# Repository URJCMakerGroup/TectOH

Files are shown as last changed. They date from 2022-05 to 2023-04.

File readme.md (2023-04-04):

# Tectonic Open Hardware (TectOH) Sandbox

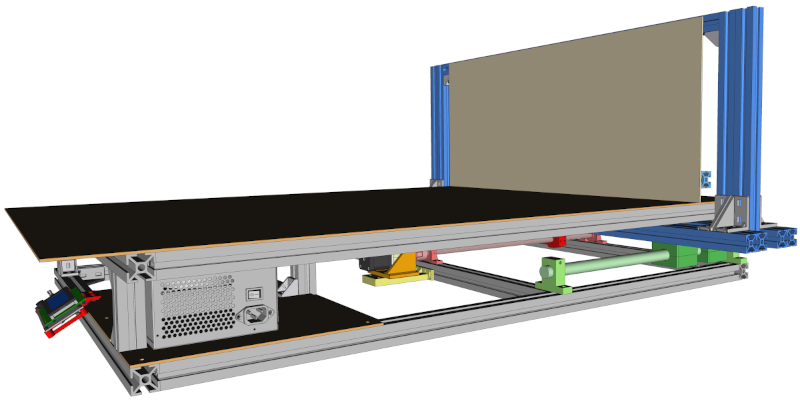
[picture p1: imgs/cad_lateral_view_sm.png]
Sandbox CAD image


Low-cost Open-Hardware scientific and educational device for tectonic analogue modelling. See Wikipedia entry on [tectonic analogue modeling](https://en.wikipedia.org/wiki/Analogue_modelling_%28geology%29).

It can move at speeds from 1 mm/h to 100 mm/h.

The stroke of the gantry is 270 mm but it can be easily customized for other lengths.

The cost of the components is no more than 500 €, although for increased performance, precision components can be used at higher cost.

There are some [optional components](#distance-monitoring) for **measuring the distance** that would increase the cost.

It is not too complicated to build. It should be simpler than building a 3D printer or CNC.

For a more theoretical information about the system and detailed explanations of the experiments, you can check the paper:
[Designing Low-Cost Open-Hardware Electromechanical Scientific Equipment: A Geological Analogue Modeling Sandbox](https://doi.org/10.1109/ACCESS.2023.3262617)

This is the second version of the Open Hardware Sandbox. [Link to the first version](https://github.com/URJCMakerGroup/TFG-Cristina-Fernandez)

----

## License

Hardware License: [CERN-OHL-S 2.0](cern_ohl_s_v2.txt)

Software License: [LGPL 3.0 or later](License.md)

Documentation License: [CC BY 4.0](https://creativecommons.org/licenses/by/4.0/)

license summary

ES000033

This device is [certified open hardware](https://certification.oshwa.org/es000033.html) by the [Open Source Hardware Association](https://www.oshwa.org/).

----

## Bill of materials

It is about 500€ without taxes and shipping costs.

There could be cheaper alternatives in your area.

You can use more expensive mechanical components to increase the overall precision of the system

[Sandbox bill of materials (.ods file)](tectoh_bom.ods)

----

## Assembly

[Sandbox assembly](./assembly/.)

----

## Firmware

[Arduino code of the Sandbox](./firmware/.)

----

## Distance monitoring

[Optical or magnetic linear sensor](./optional/.) can be included in the Sandbox to monitor the displacement.
These are optional subsystems, but they are very helpful to calibrate the Sandbox.

This section includes graphs of the **results** and Python scripts to analyze the data from the magnetic sensor.

----

## User guide

[Sandbox user guide](./userguide/.)

----

## Pictures

### Sandbox experiment

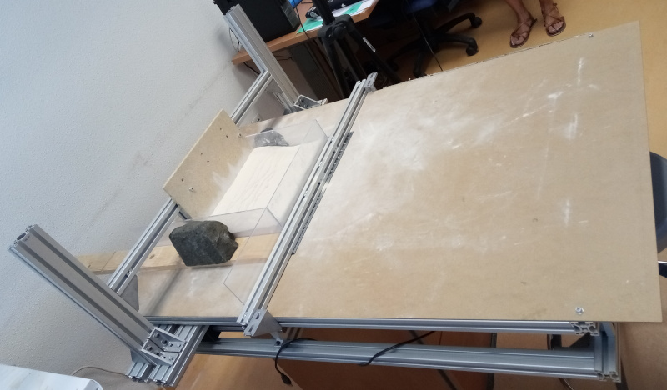
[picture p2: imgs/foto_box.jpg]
Experiment


### The Sandbox pushing a 10-kg sandpile

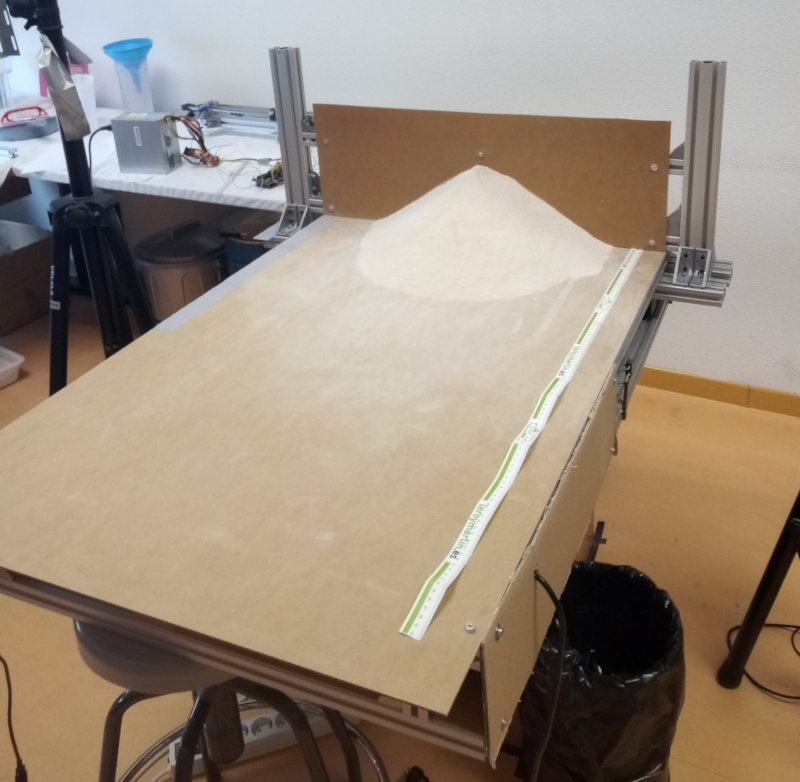
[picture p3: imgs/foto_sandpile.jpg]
Picture 10-kg sandpile


The whole experiment took 3 hours and 45 minutes, the following sequence is fast-forwarded.

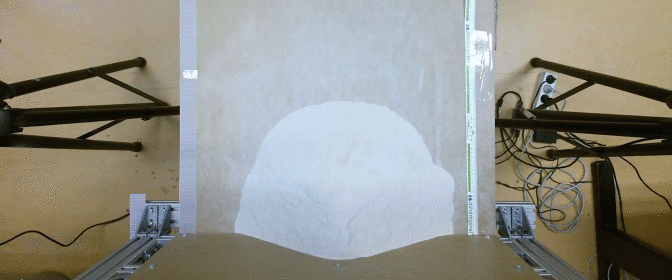
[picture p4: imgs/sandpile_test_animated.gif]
Sandpile test


### The Sandbox pushing a 5-kg sand load constrained within a box

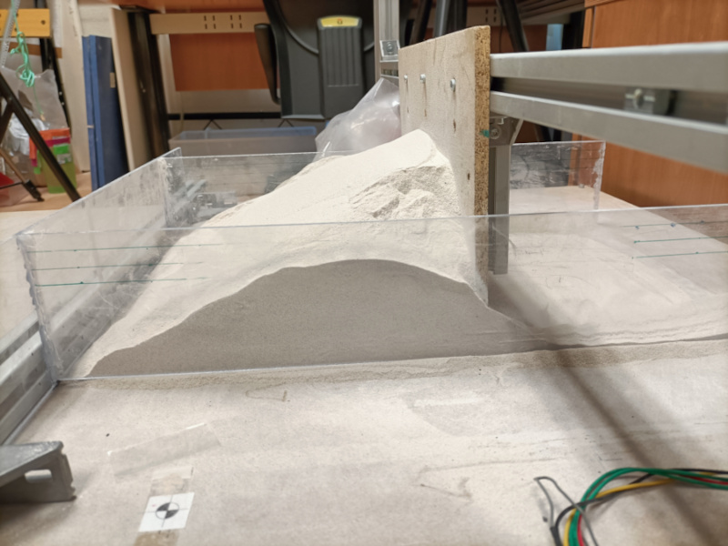
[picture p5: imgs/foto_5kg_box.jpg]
Picture 5-kg box


### The Sandbox in a geological experiment

The experiment took 4 hours (at the end the camera was moved)

Sandpile test

----

## Contributors

This work has been developed at [Universidad Rey Juan Carlos](https://www.urjc.es/) in Spain. It has been a collaboration between the Area of Electronic Technology and the group [Tecvolrisk](https://tecvolrisk.wixsite.com/website) of the Area of Geology.

### Area of Electronic Technology:

- [Felipe Machado](https://github.com/felipe-m/)
- [Rubén Nieto](https://gestion2.urjc.es/pdi/ver/ruben.nieto)
- [Susana Borromeo](https://gestion2.urjc.es/pdi/ver/susana.borromeo)

### Tecvolrisk (Area of Geology)

- [Marta Rincón](https://gestion2.urjc.es/pdi/ver/marta.rincon)
- [Sandra González-Muñoz](https://tecvolrisk.wixsite.com/website/sandra-gonz%C3%A1lez-mu%C3%B1oz)
- [Fidel Martín-González](https://gestion2.urjc.es/pdi/ver/fidel.martin)

### Students

Some students have collaborated in the project doing their capstone project in Industrial Engineering.

- [Adrián Zeus Román](https://github.com/zeus97roman/tfg): Initial project
- [Cristina Fernández García](https://github.com/cfg97/TFG-Cristina-Fernandez): Finished first version
- [David Muñoz Bernal](https://github.com/davidmubernal/MakerWorkbench): FreeCAD workbench that includes many CAD parts of the project 
- [Javier Letón](https://github.com/jleton10/TFG_Javier_Leton): Added the linear optical sensor
- [Alicia Merchán](https://github.com/AliciaMH/TFGAliciaMerchan): future work in adding a second degree of freedom

----

## Citation

If you use this hardware, you may want to cite the research article:
[Designing Low-Cost Open-Hardware Electromechanical Scientific Equipment: A Geological Analogue Modeling Sandbox](https://doi.org/10.1109/ACCESS.2023.3262617)

F. Machado et al., "Designing Low-Cost Open-Hardware Electromechanical Scientific Equipment: A Geological Analogue Modeling Sandbox," in IEEE Access, vol. 11, pp. 31716-31746, 2023, doi: 10.1109/ACCESS.2023.3262617.

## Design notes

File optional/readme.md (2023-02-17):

# Optional components

He have used two linear sensor to measure the displacement:

- Optical linear sensor
- [High-resolution magnetic sensor](#high-resolution-magnetic-sensor)

----

## Optical linear sensor

One is a optical linear sensor that has been savaged from an old printer. The sensor is 150 LPI (lines per inch) so it has a resolution around 169 μm per line.

The Arduino code includes the reading and display of the current position. However, since this component is optional, the Sandbox will work even if it is not installed.

The optical sensor that has been used is similar to the [AEDS-962x](./linear_optical_sensor/aeds-962x_150lpi.pdf)

The sensor needs a small circuit to work and to install it requires some soldering skills, especially if you to take it out from a printer.

A 330 Ohm resistor has to be included between 5V and the led emitter of the sensor. As shown in the following figure:

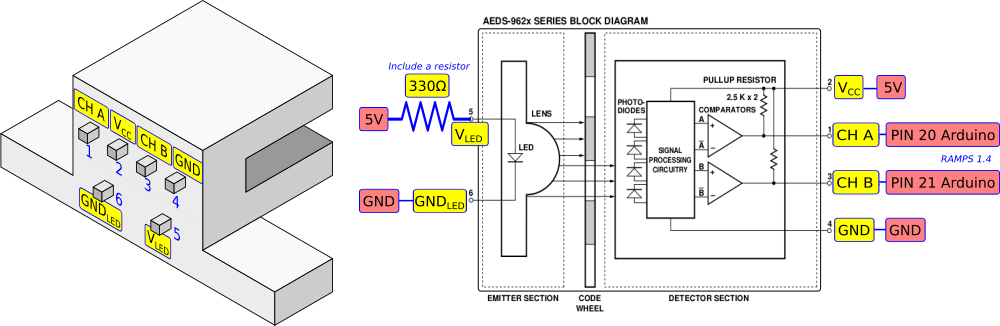
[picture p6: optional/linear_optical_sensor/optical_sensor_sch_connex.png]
Sensor connection


We have used a simple board to solder the sensor pins and the 330Ω resistor.

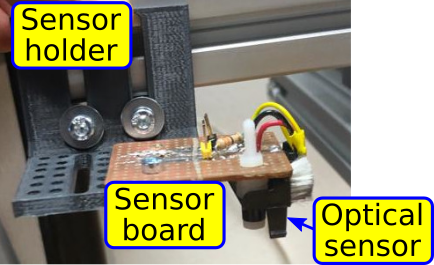
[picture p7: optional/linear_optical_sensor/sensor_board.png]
Sensor board


The following pictures show how the optical codestrip and the sensor is arranged

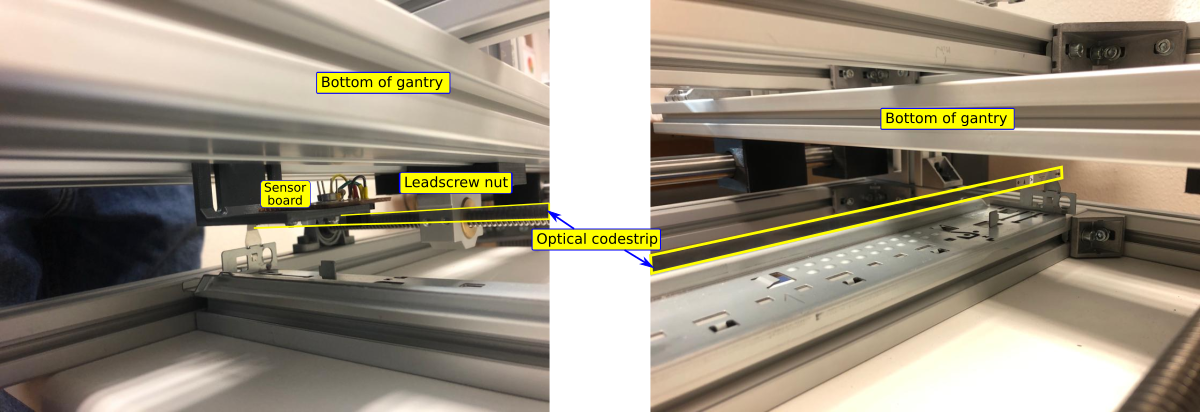
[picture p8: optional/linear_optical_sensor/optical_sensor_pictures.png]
Optical sensor arrangement


More information about these sensors:

- https://reprap.org/wiki/Optical_encoders_01
- https://cuverita.wordpress.com/2013/06/30/how-to-master-an-hp-printer-optical-encoder-carriage/

If you are going to buy one, maybe you could get the HEDS-973x Series. **Disclaimer:** We have not tried them, but they seem similar, and even simpler because the led do not have an independent power supply.

[HEDS-973x](./linear_optical_sensor/heds_973x.pdf)

----

## High resolution magnetic sensor

Since it is a high resolution sensor (less than 500 nm), the sensor will constantly update the measurement, as a consequence, it would demand too much attention from the Arduino and the system would not work properly. 
To solve this problem, we have used an external FPGA to measure the position. This sensor has been used only to validate the positional accuracy of the system.

We have used the breakout board, so it is not necessary to solder the chip, and it came with a magentic strip. The strip is small, but enough to make the experiments.

This is the [datasheet](./as5311_magn_sens/as5311_board.pdf) of the AS5311-TS-EK-AB adapter board.

And some links to suppliers where you can buy it:

- [Digikey](https://www.digikey.es/en/products/detail/ams-osram/AS5311-TS-EK-AB/3828353)
- [RS](https://es.rs-online.com/web/p/kits-de-desarrollo-de-sensores/2329691)
- [Mouser](https://eu.mouser.com/ProductDetail/ams-OSRAM/AS5311-TS_EK_AB?qs=Rt6VE0PE%2FOfQFCqoE7AuPw%3D%3D)
- [Farnell](https://es.farnell.com/ams-osram-group/as5311-ts-ek-ab/kit-placa-adapt-sensor-de-posici/dp/3976997?st=as5311)

More information on how the sensor works, the source code of the interface, and the Python scripts to analyze the received data, can be found in this folder:

[High-resolution linear magnetic sensor AS5311](./as5311_magn_sens/.)

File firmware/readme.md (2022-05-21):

# Arduino TectOH

Basic firmware Arduino code for the Sandbox.

You need to include some libraries. To install libraries, follow this [link](https://docs.arduino.cc/software/ide-v1/tutorials/installing-libraries), or open the IDE and click to the "Sketch" menu and then `Include Library > Manage Libraries`.

- TimerOne.h: https://www.arduino.cc/reference/en/libraries/timerone/
- TimerThree.h: https://www.arduino.cc/reference/en/libraries/timerthree/
- TimerFour.h: https://www.arduino.cc/reference/en/libraries/timerfour/
- LiquidCrystal.h: You don't need to add this library, as it is usually included. https://www.arduino.cc/reference/en/libraries/liquidcrystal/

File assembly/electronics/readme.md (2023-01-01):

# Electronic Assembly

## 1. Tools

Since you will need to make your own cables, you will need a crimping tool like these:

- https://www.pololu.com/product/1928
- https://www.electrocomponentes.es/crimpadoras/917-crimpadora-sn-01bm-prensa-terminales-dupont-awg-28-20-crimper-tool.html
- https://solectroshop.com/es/crimpadoras/1822-sn-28b-dupont-terminal-crimpadora.html

There are some tutorials to make custom connectors:

- https://www.instructables.com/Dupont-Crimp-Tool-Tutorial/
- https://youtu.be/GkbOJSvhCgU
- https://youtu.be/K7Qb3DzIX3s

Also you may need a soldering tool and a soldering iron and solder, to solder the cables to the enstops.

## 2. Put the jumpers in the motor driver socket of RAMPS 1.4

RAMPS 1.4: [https://reprap.org/wiki/RAMPS_1.4](https://reprap.org/wiki/RAMPS_1.4)

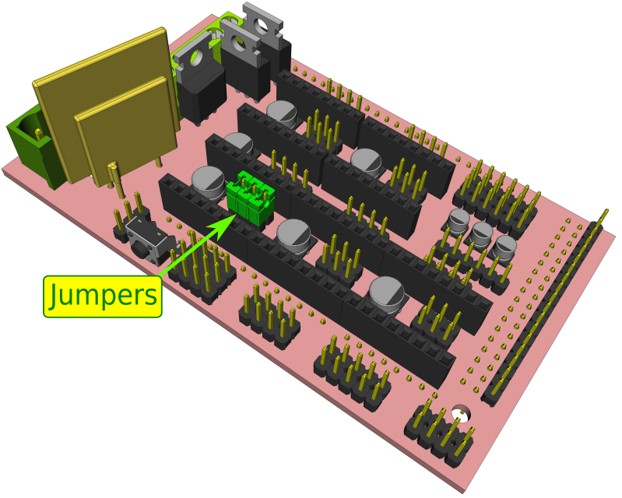
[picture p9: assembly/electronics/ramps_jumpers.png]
RAMPS-jumpers


## 3. Attach the RAMPS 1.4 to the Arduino board and attach the motor driver to the RAMPS

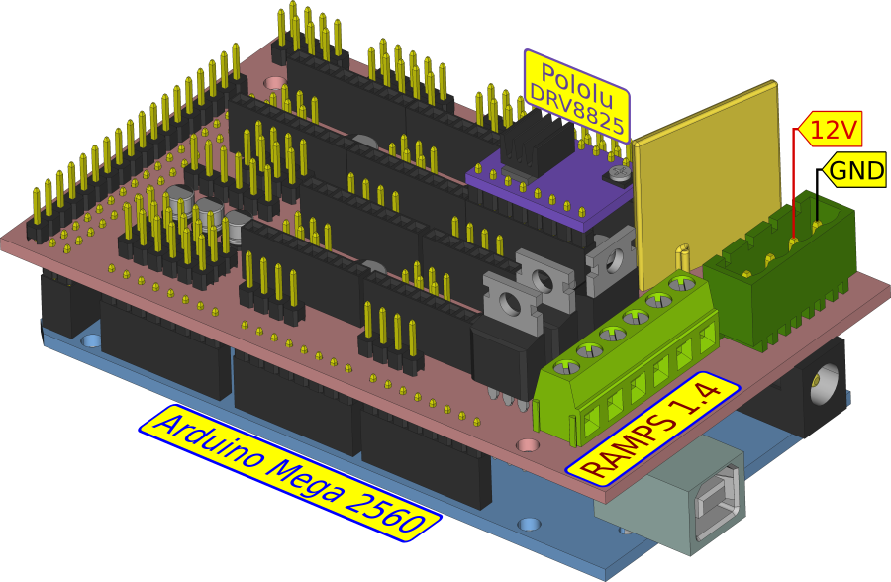
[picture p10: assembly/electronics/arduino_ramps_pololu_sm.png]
Arduino-RAMPS-DRV8825


Pay attention on the motor driver pinout, do not put it upside-down.
The Pololu DRV8825 and the A4988 have the trimmer in different positions

- Pololu DRV8825: [https://www.pololu.com/product/2133](https://www.pololu.com/product/2133)
- Pololu A4988: [https://www.pololu.com/product/1182](https://www.pololu.com/product/1182)

[Larger image: Arduino-RAMPS-DRV8825](./arduino_ramps_pololu.png)

## 4. Connect the elements as in the figure

If the power suppy is computer ATX, its green cable should be tied to ground (black)

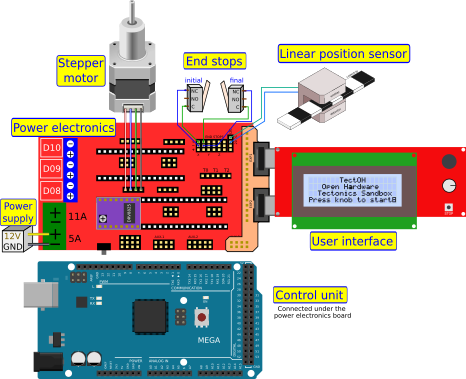
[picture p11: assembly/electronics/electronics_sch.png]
Electronics schematic


[Larger image of electronics schematic](./electronics_sch_big.png)

The section of the [optional components](../../optional/.) has more information on how to connect the optical sensor.

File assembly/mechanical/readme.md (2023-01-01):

# Sandbox assembly

Besides these instructions assembly section, the CAD source file of the Sandbox can be used as a guide for assembling the Sandbox.

You can open the source file with [FreeCAD](https://www.freecadweb.org/) (free and opensource): [tectoh.FCStd](../cad/freecad/tectoh.FCStd)

We couldn't upload the step file because it was too large for github.

## Step A: Assembly of the structure's lower base
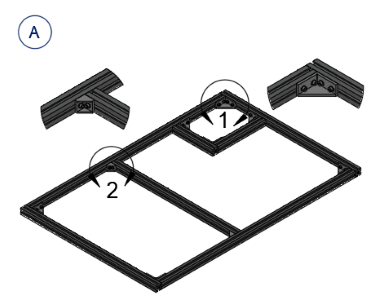
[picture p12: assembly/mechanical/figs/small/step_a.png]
Step A


[Larger image](figs/big/step_a.png)

### Parts
| Components | Quantity | 
|-----------------|:--------------:|
| Aluminum profile Type B Slot 8 (30x30x1060 mm) |   2 units  |
| Aluminum profile Type B Slot 8 (30x30x740 mm)  |   2 units   |
| Aluminum profile Type B Slot 8 (30x30x680 mm)  |   1 unit  |
| Aluminum profile Type B Slot 8 (30x30x260 mm)  |   1 unit  |
| Aluminum profile Type B Slot 8 (30x30x220 mm)  |   1 unit  |
| Bracket Type B (30x60 mm)  |   7 units  |
| Bracket Type B (30x30 mm)  |   2 units  |
| M5x14 mm Screw  |   32 units  |
| T-nut for slot 8 type B with spring (M5)   |   32 units  |
| Washer 5 mm  |   32 units  |

### Tools
* Allen Wrench 4

## Step B: Cutout of the lower clamping board 
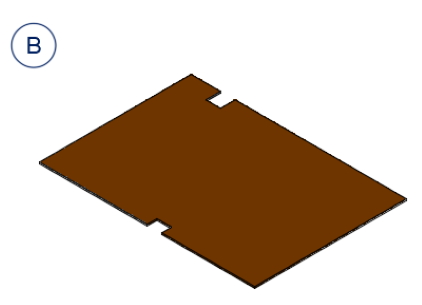
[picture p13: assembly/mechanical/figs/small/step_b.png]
Step B


### Parts
| Components | Quantity | 
|-----------------|:--------------:|
| Wooden Board (440x310x3 mm) |   1 unit  |

### Tools
* Hacksaw
* Keyhole saw
* Rasp

## Step C: Placement of the lower wooden board
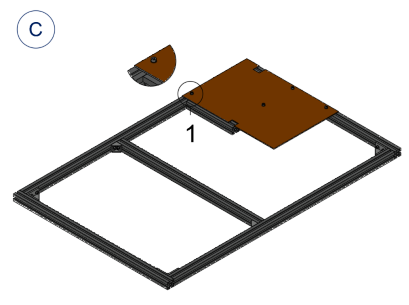
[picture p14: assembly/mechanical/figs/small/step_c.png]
Step C

[Larger image](figs/big/step_c.png)

### Parts
| Components | Quantity | 
|-----------------|:--------------:|
| Wooden Board (440x310x3 mm) |   1 unit  |
| M5x16 mm Screw  |   4 units  |
| T-nut for slot 8 type B with spring (M5)   |   4 units  |
| Washer 5 mm  |   4 units  |

### Tools
* Allen Wrench 4
* Drill

## Step D: Aluminum profiles's positioning to give height to the structure
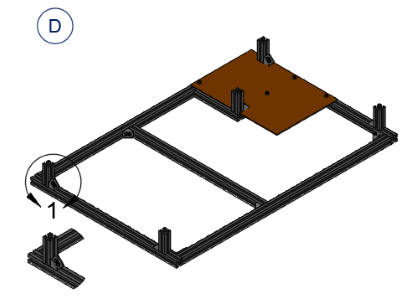
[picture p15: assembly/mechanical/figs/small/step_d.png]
Step D

[Larger image](figs/big/step_d.png)

### Parts
| Components | Quantity | 
|-----------------|:--------------:|
| Aluminum profile Type B Slot 8 (30x30x90 mm) |   5 units  |
| Bracket Type B (30x30 mm)  |   5 units  |
| M5x14 mm Screw  |   8 units  |
| M5x16 mm Screw  |   2 units  |
| T-nut for slot 8 type B with spring (M5)   |   10 units  |
| Washer 5 mm  |   10 units  |

### Tools
* Allen Wrench 4

## Step E: Kinematic pairs's assembly
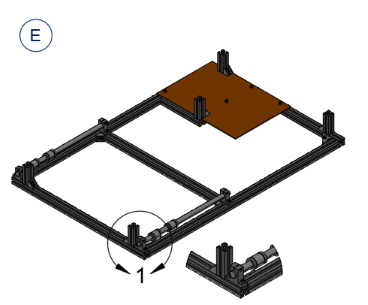
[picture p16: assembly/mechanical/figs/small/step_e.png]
Step E

[Larger image](figs/big/step_e.png)

### Parts
| Components | Quantity | 
|-----------------|:--------------:|
| Steel shaft Ø20 mm L500 mm |   2 units  |
| Shaft supports SH20/SK20 |   4 units  |
| Lineal bearing 20 mm LME20UU |   4 units  |
| T-nut for slot 8 type B with spring (M5)   |   8 units  |
| M5x14 mm Screw  |   8 units  |
| M5x25 mm Screw  |   4 units  |

### Tools
* Allen Wrench 4

## Step F: Drive system's assembly
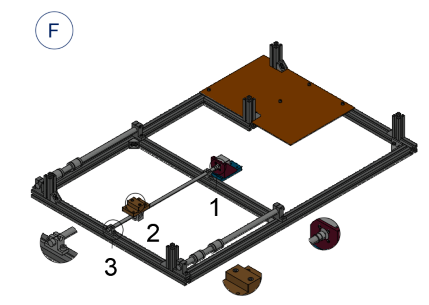
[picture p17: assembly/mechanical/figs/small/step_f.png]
Step F

[Larger image](figs/big/step_f.png)

### Parts
| Components | Quantity | 
|-----------------|:--------------:|
| Spindle TR12x3 mm |   1 unit  |
| 90º flange bearing  |   2 units  |
| Flexible coupling  |   1 unit  |
| Trapezoidal lead nut for spindle 12x3 R  |   1 units  |
| M3x14 mm Screw  |   4 units  |
| M4x25 mm Screw  |   4 units  |
| M5x12 mm Screw  |   2 units  |
| M5x20 mm Screw  |   2 units  |
| M6x12 mm Screw  |   4 units  |
| Hexagonal Nut M4  |   2 units  |
| T-nut for slot 8 type B with spring (M5)   |   2 units  |
| T-nut for slot 8 type B with spring (M6)   |   4 units  |
| Washer 5 mm  |   2 units  |

### Tools
* Allen Wrench 4
* Allen Wrench 5

## Step G: Gantry assembly

The gantry can be assembled in different ways depending on the experiment.

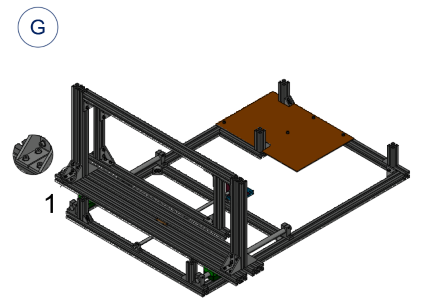
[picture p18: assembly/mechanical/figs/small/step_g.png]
Step G

[Larger image](figs/big/step_g.png)

### Parts
| Components | Quantity | 
|-----------------|:--------------:|
| Aluminum profile Type B Slot 8 (30x30x800 mm) |   1 unit  |
| Aluminum profile Type B Slot 8 (30x30x740 mm) |   1 unit  |
| Aluminum profile Type B Slot 8 (30x30x244 mm) |   2 units  |
| Aluminum profile Type B Slot 8 (30x60x980 mm) |   2 units  |
| Aluminum profile Type B Slot 8 (30x60x400 mm) |   2 units  |
| Bracket Type B (30x60 mm)  |   14 units  |
| M5x14 mm Screw  |   56 units  |
| M5x18 mm Screw  |   4 units  |
| M5x40 mm Screw  |   16 units  |
| T-nut for slot 8 type B with spring (M5)   |   76 units  |
| Washer 5 mm  |   56 units  |

### Tools
* Allen Wrench 4

## Step H: Assembly of the structure's upper base
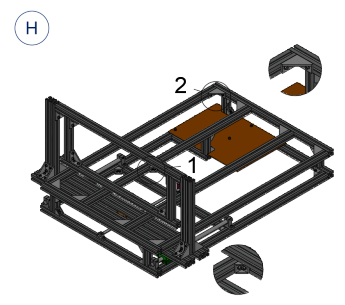
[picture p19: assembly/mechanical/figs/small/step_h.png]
Step H

[Larger image](figs/big/step_h.png)

### Parts
| Components | Quantity | 
|-----------------|:--------------:|
| Aluminum profile Type B Slot 8 (30x30x1060 mm) |   4 units  |
| Aluminum profile Type B Slot 8 (30x30x740 mm) |   2 units  |
| Aluminum profile Type B Slot 8 (30x30x240 mm) |   1 unit  |
| Bracket Type B (30x30 mm)  |   7 units  |
| Bracket Type B (30x60 mm)  |   8 units  |
| M5x14 mm Screw  |   46 units  |
| T-nut for slot 8 type B with spring (M5)   |   46 units  |
| Washer 5 mm  |   46 units  |

### Tools
* Allen Wrench 4

## Step I: Placement of the upper wooden board
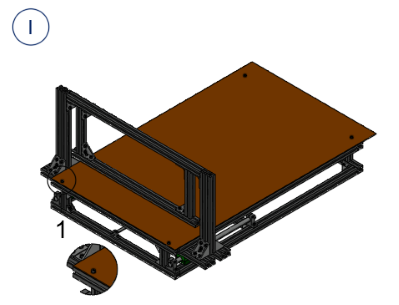
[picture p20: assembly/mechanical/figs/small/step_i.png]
Step I

[Larger image](figs/big/step_i.png)

### Parts
| Components | Quantity | 
|-----------------|:--------------:|
| Wooden Board (1200x740x3 mm) |   1 unit  |
| M5x16 mm Screw  |   4 units  |
| T-nut for slot 8 type B with spring (M5)   |   4 units  |
| Washer 5 mm  |   4 units  |

### Tools
* Allen Wrench 4
* Drill

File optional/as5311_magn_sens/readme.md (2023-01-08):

# Displacement monitoring with FPGA and the AS5311 magnetic linear sensor

The [AS5311 sensor](https://ams.com/en/as5311) is interfaced with an external FPGA board because the Arduino could not handle the Sandbox operation at the same time.
We have used an FPGA board, but a high-performace microcontroller could be used.

## VHDL design for interfacing the AS5311 with an FPGA

[VHDL design for interfacing the high resolution magnetic linear sensor AS5311](./vhdl/.)

The interface with the sensor is explained. Then the FPGA sends the data to a computer.

----

## Magnetic sensor analysis

In this folder we have the [Python scripts](./magn_sensor_analysis) that analyse the data from the magnetic sensor and plots it.

A link to the data from the sensor is also in the folder

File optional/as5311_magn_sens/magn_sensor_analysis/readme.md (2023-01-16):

# AS5311 high-resolution sensor data analysis

## Dataset

Due limited space in github, the dataset is located in [Zenodo](https://doi.org/10.5281/zenodo.7513730), in this link there are two kind of files:

*   **bin**: raw binary files received from the AS5311 high resolution sensor. Although this sensor sends 12 bit data, we have truncated the most significant bits and receive only 8 bits (one byte). Therefore, each byte of these binary files is a measurement of the distance. Each distance increment corresponds to ~0.488nm (2mm/2048)
*   **csv**: csv files that can be opened with any spreadsheet app, such as Libreoffice Calc or Microsoft Excel, or even with a text editor. This file contains the processed data from the binary files. These files have been generated with the proc\_magn\_sensor.py Python script. These files have som columns, which are:
    *   index: measurement number
    *   time in milliseconds: each measurement is taken every 250 us
    *   median2: in micrometers, since the sensor may jitter, we have applied the median filter twice. All the data has been subtracted to the lowest value, making the lowest value equal to zero.
    *   median1: in micrometers, median filter only applied once. All the data has been subtracted to the lowest value, making the lowest value equal to zero.
    *   mean: in micrometers, mean filter. All the data has been subtracted to the lowest value, making the lowest value equal to zero.
    *   mean int: in micrometers, mean filter rounded to an integer value. All the data has been subtracted to the lowest value, making the lowest value equal to zero.
    *   orig\_base: this is not in micrometers, but in the units of the sensor (~0.488nm). The only processing done is that when there is an overflow of 255 to 0, or from 0 to 255, it adds the overflow to continue the trend. All the data has been subtracted to the lowest value, making the lowest value equal to zero.
    *   original: this is the data received from the sensor with no processing, each value is ~0.488nm
    *   mean2: in micrometers, mean filter applied twice. All the data has been subtracted to the lowest value, making the lowest value equal to zero.

There are two set of experiments:

*   Experiments with no load. These files start with _noload\__  
    In these experiments the gantry is moved 1 mm alternatively to the front and then reversing direction. Moving in this alternate way a few times. There are five experiments each of them with a different speed: v= 10 mm/h; 25 mm/h; 50 mm/h; 82 mm/h and 100 mm/h. The name of the file indicates the speed:
    1.  noload\_100mmh\_1mm: FBFBF: 1mm forth, 1mm back, 1mm forth, 1mm back, 1 mm forth
    2.  noload\_25mmh\_1mm: FBFFBBFB
    3.  noload\_50mmh\_1mm: FBFBFB
    4.  noload\_82mmh\_1mm: FBFBFB
    5.  noload\_100mmh\_1mm: FBFBFB
*   Experiments with a 5kg sand load. These files start with _load5kg\__
    1.  load5kg\_25mmh\_5mm: moving 5kg at 25mm/h a distance of 5mm
    2.  load5kg\_25mmh\_10mm: moving 5kg at 25mm/h a distance of 10mm
    3.  load5kg\_25mmh\_20mm: moving 5kg at 25mm/h a distance of 20mm
    4.  load5kg\_75mmh\_20mm: moving 5kg at 75mm/h a distance of 20mm
    5.  load5kg\_75mmh\_50mm: moving 5kg at 75mm/h a distance of 50mm
    6.  load5kg\_100mmh\_25mm: moving 5kg at 100mm/h a distance of 20mm
    7.  load5kg\_100mmh\_50mm: moving 5kg at 100mm/h a distance of 50mm

---

## Python scripts for processing the data

In order to process the raw binary data (.bin files of the dataset), the python script [proc_magn_sensor.py](./proc_magn_sensor.py) converts the binary file into the .csv file. These .csv files are available in the dataset. 

If you want to run the script, open it and uncomment the line related to the file you want to analyze. Then run it with this command

```
>> python3 proc_magn_sensor.py
```

Once you have the .csv file (that you can also download from the dataset, you can plot the graph, with [plot.py](./plot.py)

Also, you can plot the raw binary file to take a look to it, with [show_raw.py](./show_raw.py), for this script you have to introduce the binary file as a parameter.

----

## Plots of No-load experiments

Following, the plots of each no-load experiment are shown

###  No-load 10mmh 1mm FBFBF

1mm forth, 1mm back, 1mm forth, 1mm back, 1mm forth:

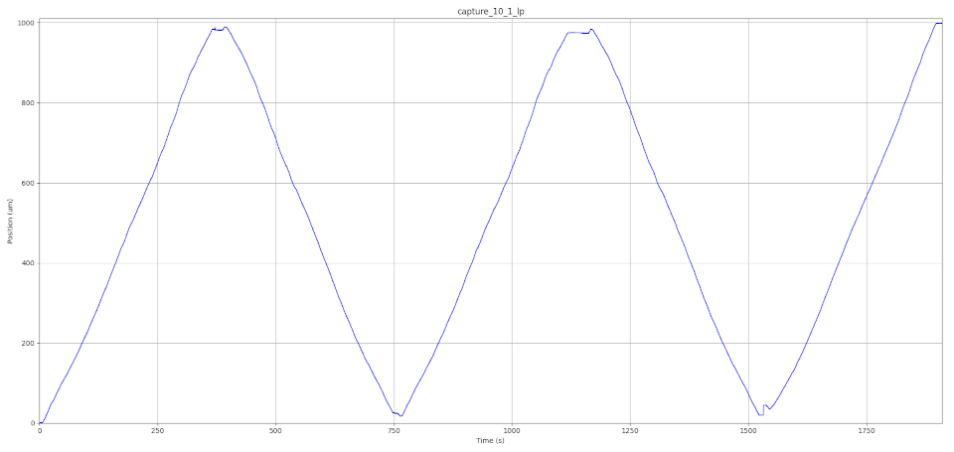
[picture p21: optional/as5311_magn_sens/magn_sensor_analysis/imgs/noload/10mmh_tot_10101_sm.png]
10mmh_tot_10101_sm


[larger image](imgs/noload/10mmh_tot_10101.png)

###  No-load 25mm/h 1mm FBFFBBFB

1mm forth, 1mm back, 1mm forth, 1mm forth, 1mm back, 1mm back, 1mm forth, 1mm back:

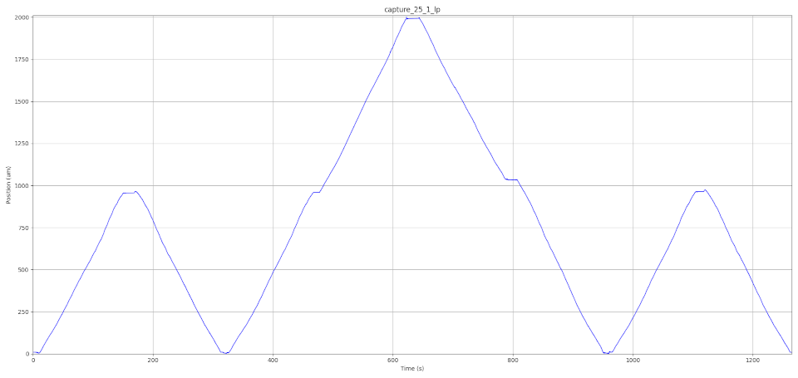
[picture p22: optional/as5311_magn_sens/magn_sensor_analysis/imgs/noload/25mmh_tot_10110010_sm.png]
25mmh_tot_10110010_sm


[larger image](imgs/noload/25mmh_tot_10110010.png)

###  No-load 50mm/h 1mm FBFBFB

1mm forth, 1mm back, 1mm forth, 1mm back, 1mm forth, 1mm back:

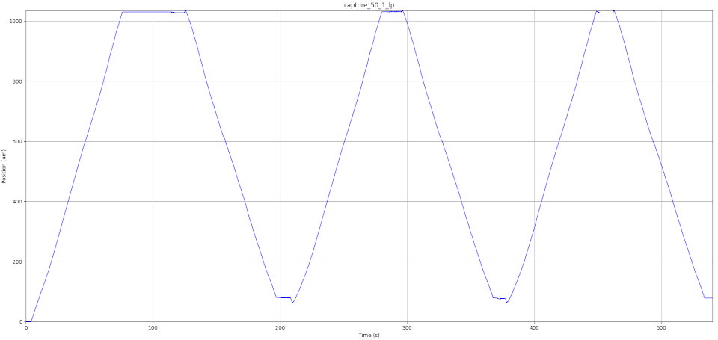
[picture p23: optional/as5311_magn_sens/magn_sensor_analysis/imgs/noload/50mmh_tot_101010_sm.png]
50mmh_tot_101010_sm


[larger image](imgs/noload/50mmh_tot_101010.png)

###  No-load 82mm/h 1mm FBFBFB

1mm forth, 1mm back, 1mm forth, 1mm back, 1mm forth, 1mm back:

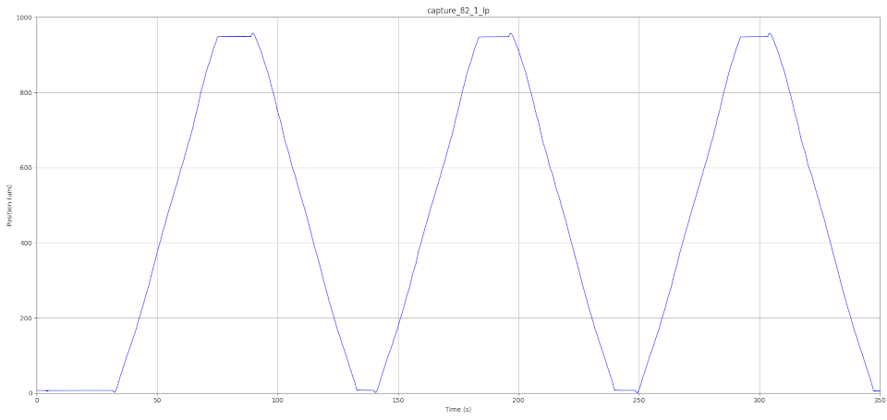
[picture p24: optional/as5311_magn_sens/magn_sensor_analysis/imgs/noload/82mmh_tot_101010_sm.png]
82mmh_tot_101010_sm


[larger image](imgs/noload/82mmh_tot_101010.png)

###  No-load 100mm/h 1mm FBFBFB

1mm forth, 1mm back, 1mm forth, 1mm back, 1mm forth, 1mm back:

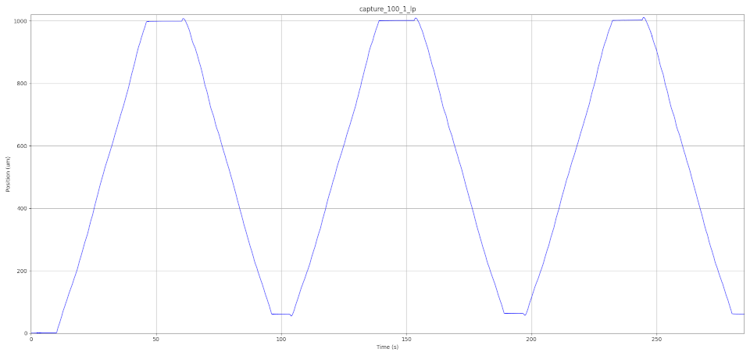
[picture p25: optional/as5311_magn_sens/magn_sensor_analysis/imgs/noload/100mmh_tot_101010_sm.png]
100mmh_tot_101010_sm


[larger image](imgs/noload/100mmh_tot_101010.png)

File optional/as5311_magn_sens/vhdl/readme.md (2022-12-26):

# VHDL

## as5311_uart

VHDL code to test the displacement rate of the Sandbox.
It controls the [AS5311 linear position  sensor](https://ams.com/en/as5311) and sends the position data to the UART (via USB).

The linear sensor has a magentic strip with 2mm pole pair and sends the absolute position within this 2mm in 12 bits -> Resolution 2mm/4096 = 0.488 um

The linear sensor sends the data via SSI to the FPGA. Each SSI message has 18 bits, which 12 bits corresponds to the positional data. There are other information bits in the message.

The FPGA receives this 12 bit positional data to the UART.

AS5311 has a sampling rate about 10kHz. However, due to the slow speeds of the Sandbox, we don't need sampling at such higher rates.

The SSI clock is provided by the FPGA. The maximum frequency is 1MHz (T=1us). Since the SSI sends 18 bits, and there are some other timming constraints, aproximately, the message frequency is around 20 times lower. The whole message has a frequency around 50kHz (20 us per message). But it is 12 bit message.

Since we don't need such high rates due to the low speed of the Sandbox, we use a frequency of 100kHz (T=10us). So it is safer to send through the cables. This leads to a message frequency of 5kHz (200 us per message).

We even lower the **message frequency to 4kHz** (250 us per message). Therefore, **each sample is taken every 250 us**. 4000 samples per second.

The Sanbox has a 3mm lead, a 200 pole stepper motor, a 50.9 gear reduction, and the motor moves using halfsteps (HS). This makes that the gantry advances 147 nm per halfstep.

Since the linear sensor resolution is 488 nm, we need to move 3.31 halfsteps for the sensor to notice a change in position. Therefore, the sensor is not capable of sensing just one halfstep.

When the motor is not slewing, and using microstepping, the motor takes around **6.5 ms per halfstep**. 
Therefore, since we are sampling every 250 us, we would take around 25 samples for each halfstep. Since the distance resolution of the sensor is three times larger that the distance of a halfstep. These 25 samples should be of the same value, or at most would vary in just one unit (of the 12 bits of the position).

Given these slow speeds relative to the sensor resolution, at 6.5 ms per halfstep, the sensor will notice a change every 85.75 samples.

Since the UART sends 8 bits, we are going to just send the 8-lsb, and the computer will easily make the calculations. Since from each of the sendings, the variation would be one unit at most.

The UART sends the 8-bit position at 115200 bauds, which is 11520bytes per second. That is, the message frequency 11.52 kHz (11.52 kB/s).
Since this frequency is higher than the 4kHz message frequency of the linear sensor. We can just directly send the position value received from the sensor without the need of using a buffer. We could even send to messages for the 4 MSB that are not being send. But there is no need to do that, because the changes in position are of one unit at most. So the computer can easily figure out the position.

The data can be received by a terminal such as RealTerm. Setting the baudrate to 115200. Selecting the adequate port and saving the data received in a file (in Capture tab).

---

The VHDL design includes modules to control a motor, to move it while doing the test. However, we don't need it, since the motor is controlled by the Arduino. We have left it in case it is useful in the future.

### Inputs and Outputs

- btn_reset: is the reset
- btnc (central): initialize the millimiter count
- sw(0): determines if we are requesting the AS5133 the position
or the magnetic field. **Should be ON (HIGH '1') to request the position**
- sw(1): motor enable. OFF (LOW '0') is active

Leds show the status bits of the AS5311
- led(0) : parity OK
- led(1) : Mag DEC 
- led(2) : Mag INC
- led(3) : LIN
- led(4) : COF
- led(5) : OC

7 segment displays
- Display 2 down to 0: position data from the AS5311. It is 12 bit, so 4 bits each display. Hexadecimal.
- Display 4 down to 3: millimiters distance in Hex. 8 bit. There is overlap with the 12 bit position data, because the position data divides 2mm in 12 bits. So the MSB should be the same as the millimeters unit.
- Displays 7 down to 5: Field data of the sensor

I/O not used in this test, this is when the motor is controlled by the FPGA
- btn_r (right): a step forward
- btn_l (left): a step back
- btn_u (up): 16 steps forward
- btn_d (down): 16 steps back

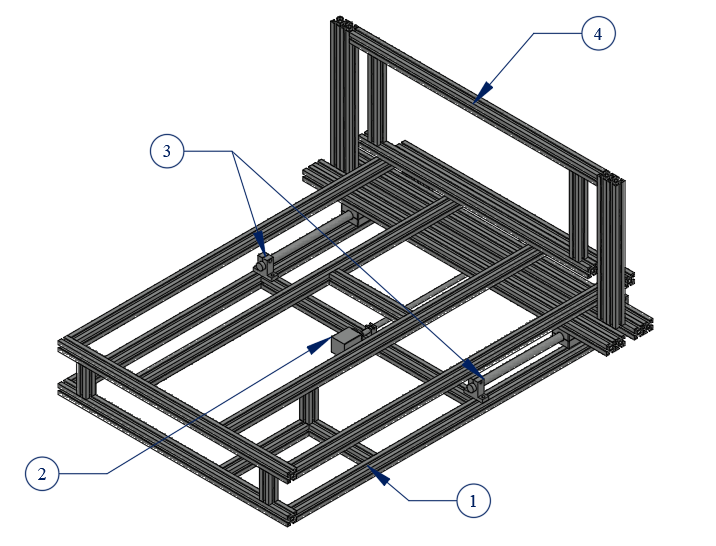
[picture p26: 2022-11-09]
assembly/mechanical/figs/big/Mesa_modelado.png

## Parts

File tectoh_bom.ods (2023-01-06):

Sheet: sanbox bill of materials
 |  | Components | Length (mm) | € / m | Unit price | Quantity | Total price | Link | Comments | Alternative:
Aluminum Profiles | 30x60 | Aluminum profile 30x60 B-Type Slot 8 | 980 | 14,52 € | 14,23 € | 2 | 28,46 € | https://www.motedis.es/en/Profile-30x60-B-Type-Slot-8
 |  | Aluminum profile 30x60 B-Type Slot 8 | 400 | 14,52 € | 5,81 € | 2 | 11,62 €
 | 30x30 | Aluminum profile 30x30 B-Type Slot 8 | 1060 | 7,98 € | 8,46 € | 6 | 50,75 € | https://www.motedis.es/en/Profile-30x30-B-Type-Slot-8
 |  | Aluminum profile 30x30 B-Type Slot 8 | 800 | 7,98 € | 6,38 € | 1 | 6,38 €
 |  | Aluminum profile 30x30 B-Type Slot 8 | 740 | 7,98 € | 5,91 € | 5 | 29,53 €
 |  | Aluminum profile 30x30 B-Type Slot 8 | 680 | 7,98 € | 5,43 € | 1 | 5,43 €
 |  | Aluminum profile 30x30 B-Type Slot 8 | 260 | 7,98 € | 2,07 € | 1 | 2,07 €
 |  | Aluminum profile 30x30 B-Type Slot 8 | 244 | 7,98 € | 1,95 € | 2 | 3,89 €
 |  | Aluminum profile 30x30 B-Type Slot 8 | 240 | 7,98 € | 1,92 € | 1 | 1,92 €
 |  | Aluminum profile 30x30 B-Type Slot 8 | 220 | 7,98 € | 1,76 € | 1 | 1,76 €
 |  | Aluminum profile 30x30 B-Type Slot 8 | 90 | 7,98 € | 0,72 € | 5 | 3,59 €
 | Optional | Aluminum profile 30x30 B-Type Slot 8 | 435 | 7,98 € | 3,47 € | 1 | 3,47 € |  | This is for the optional optical linear sensor
 | Optional | Aluminum profile 30x30 B-Type Slot 8 | 800 | 7,98 € | 6,38 € | 2 | 12,77 € |  | This is the size of the gantry, it can be useful to have another along the gantry, and also to have along the base board, as an end of the wall box (if the sand of the experiment is in a box)
 | Extra | Aluminum profile 30x30 B-Type Slot 8 | 3000 | 7,98 € | 23,94 € | 1 | 23,94 € |  | It is recommended to have different profile sizes for the gantry wall and to support the box. Cut these in different sizes
Total Aluminum profiles |  |  |  |  |  |  | 185,57 €
Brackets |  | Bracket 30x60 B-Type slot 8 |  |  | 1,68 € | 29 | 48,72 € | https://www.motedis.es/en/Bracket-30x60-B-Typ-slot-8
 |  | Bracket 30 B-Type slot 8 |  |  | 0,58 € | 20 | 11,60 € | https://www.motedis.es/en/Bracket-30-B-Type-slot-8
Profile Nuts |  | Slotted block with spring B-type slot 8 M5 |  |  | 0,24 € | 160 | 38,40 € | https://www.motedis.es/en/Slotted-block-with-spring-B-type-slot-8-M5 | Recommended to have more than needed, also M4 and M6
 |  | T-nut B-type slot 8 M5 |  |  | 0,12 € | 40 | 4,80 € | https://www.motedis.es/en/T-nut-B-type-slot-8-M5 | Recommended to have more than needed, also M4 and M6
Mechanical System |  | Precision shaft 20 mm h6 - steel - hardened and ground | 500 | 11,05 € | 5,53 € | 2 | 11,05 € | https://www.motedis.es/en/Precision-shaft-20-mm-h6-steel-hardened-and-ground
 |  | Shaft supports SH20/SK20 |  |  | 2,06 € | 4 | 8,24 € | https://www.motedis.es/en/Shaft-supports-SH20-SK20
 |  | Lineal bearing 20 mm LME20UU |  |  | 1,67 € | 4 | 6,68 € | https://www.motedis.es/en/Linear-bearing-20mm-LME20UU
 |  | Pillow Block KP001 12mm |  |  | 2,39 € | 2 | 4,78 € | https://www.motedis.es/en/Pillow-blocks-12mm-KP001
 |  | Trapezoidal threaded spindle RPTS right TR 12x3 500 mm |  |  | 6,28 € | 0,5 | 3,14 € | https://www.motedis.es/en/Trapezoidal-threaded-spindle-RPTS-right-TR-12x3
 |  | Trapezoidal lead screw nut 12x3 R red bronze with aluminum housing |  |  | 15,49 € | 1 | 15,49 € | https://www.motedis.es/en/Trapezoidal-lead-screw-nut-12x3-R-red-bronze-with-aluminum-housing
Motor |  | Nema 17 Stepper Motor Bipolar L=48mm w/ Gear Ratio 51:1 Planetary Gearbox |  |  | 35,27 € | 1 | 35,27 € | https://www.omc-stepperonline.com/nema-17-stepper-motor-bipolar-l-48mm-w-gear-ratio-51-1-planetary-gearbox-17hs19-1684s-pg51
 |  | 8mm - 12mm Flexible Jaw Coupling 25x30mm |  |  | 3,97 € | 1 | 3,97 € | https://www.omc-stepperonline.com/8mm-12mm-flexible-jaw-coupling-25x30mm-cnc-stepper-motor-shaft-coupler-mh2530-8-12
Total Profile Nuts and Mechanical System |  |  |  |  |  |  | 192,14 €
Nuts, Bolts & washers |  | M3x14 mm Bolt (DIN 912) |  |  | 0,13 € | 4 | 0,50 € | https://www.rationalstock.es/catalogo/producto/fijacion/tornillos/tornillos-cilindricos-rosca-metrica/tornillo-din-912-de-cabeza-cilindrica-con-hueco-hexagona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
 |  | M4x25 mm Bolt (DIN 912) |  |  | 0,09 € | 4 | 0,35 €
 |  | M5x12 mm Bolt (DIN 912) |  |  | 0,15 € | 6 | 0,87 €
 |  | M5x14 mm Bolt (DIN 912) |  |  | 0,03 € | 150 | 4,89 €
 |  | M5x16 mm Bolt (DIN 912) |  |  | 0,17 € | 10 | 1,73 €
 |  | M5x18 mm Bolt (DIN 912) |  |  | 0,15 € | 4 | 0,61 €
 |  | M5x20 mm Bolt (DIN 912) |  |  | 0,17 € | 2 | 0,34 €
 |  | M5x25 mm Bolt (DIN 912) |  |  | 0,13 € | 4 | 0,51 €
 |  | M5x40 mm Bolt (DIN 912) |  |  | 0,07 € | 16 | 1,10 €
 |  | Hexagonal Nut M4 |  |  | 0,0046 € | 10 | 0,05 € | https://www.rationalstock.es/catalogo/producto/fijacion/tuercas/tuercas-hexagonales/tuerca-din-934-hexagonal--de-acero-cincado-y-rosca-metrica-/20450500002
 |  | Washer M-5 (DIN 125) |  |  | 0,0031 € | 154 | 0,48 € | https://www.rationalstock.es/catalogo/producto/fijacion/arandelas/arandelas-planas/arandela-din-125-1-a-plana--de-acero-cincado-/20500500002
Total Nuts, Bolts and washers |  |  |  |  |  |  | 11,44 € |  | Always recommended to have more and different sizes
Electronics & Electrical |  | RAMPS 1.4 |  |  | 4,95 € | 1 | 4,95 € | https://www.hta3d.com/es/ramps-1-4
 |  | Arduino Mega 2560 original |  |  | 35,70 € | 1 | 35,70 € | https://store.arduino.cc/products/arduino-mega-2560-rev3 | Arduino compatible can be cheaper: 10,54 € | https://www.hta3d.com/es/mega-2560-r3-compatible
 |  | DRV8825 |  |  | 1,86 € | 1 | 1,86 € | https://www.hta3d.com/es/drv8825-controlador-para-motor-paso-a-paso,-alta-intensidad-driver | Recommended to buy more than one because they can be damaged if not handled properly, and at the beginning that may be the case
 |  | LCD smart controller |  |  | 7,02 € | 1 | 7,02 € | https://www.hta3d.com/es/pantalla-2004-lcd-smart-controller
 |  | Endstop |  |  | 0,34 € | 2 | 0,68 € | https://www.electrocomponentes.es/pulsadores/660-740-final-de-carrera-con-pletina-5a-220v-endstop-microswitch.html |  | https://es.farnell.com/multicomp/m140t01-ae0507a/microinterruptor-spdt-5a-palanca/dp/1735352?st=1735352
 |  | Heat-shrink tubing |  |  | 0,12 € | 1 | 0,12 € | https://www.hta3d.com/es/termorretractil
 |  | Wire to Board Crimp Terminal, 24AWG |  |  | 0,03 € | 25 | 0,65 € | https://www.electrocomponentes.es/dupont-254mm/447-568-conector-dupont-254mm-hembra-para-soldar-o-crimpar.html | You will need a crimping tool: https://www.pololu.com/product/1928 | Alternative: https://es.farnell.com/multicomp/2226tg/terminal-de-crimpar-24-28awg/dp/1593529 | https://www.pololu.com/product/1930
 |  | Male Crimp Pins for 0.1" Housings |  |  | 0,03 € | 25 | 0,65 € | https://www.electrocomponentes.es/dupont-254mm/448-571-conector-dupont-254mm-macho-para-soldar-o-crimpar.html | You may not need them, but they are useful | https://www.pololu.com/product/1931
 |  | 0.1" (2.54mm) Crimp Connector Housing |  |  | 0,01 € | 50 | 0,74 € | https://www.electrocomponentes.es/dupont-254mm/429-532-carcasa-plastico-dupont-254mm-1p.html | You don’t need 50, but they are useful and cheaper if bought in larger quantities | https://www.pololu.com/product/1900
 |  | 0.1" (2.54mm) Crimp Connector Housing: 1x4-Pin |  |  | 0,04 € | 20 | 0,74 € | https://www.electrocomponentes.es/dupont-254mm/432-537-carcasa-plastico-dupont-254mm-4p.html | You can use four of 1x1 instead | https://www.pololu.com/product/1903
 |  | Electrical cable m |  |  | 0,419 | 10 | 4,19 € | https://es.farnell.com/pro-power/pp001248/tri-rated-wire-0-5mm2-light-blue/dp/2528150
 |  | Power source ATX 500W |  |  | 12,20 € | 1 | 12,20 € | https://www.pccomponentes.com/unykach-fuente-de-alimentacion-atx-500w | Any ATX power source, or many others are valid. Should provide 12V, 500W is more than enough, smaller power would be ok. Recommended one with a switch, so it can be used as emergency stop switch
Total Electrical and Electronics |  |  |  |  |  |  | 69,49 €
 |  | Wooden Board (1200x740x3 mm) |  |  |  | 1 | 25,00 € |  | Base of the Sandbox, where the sand is placed
 |  | Wooden Board (440x310x3 mm) |  |  |  | 1 | 4,00 € |  | Base of the electronics: Power source, Arduino and LCD
 |  | Wooden Board (740x327x3 mm) |  |  |  | 1 | 6,00 € |  | Different sizes to be attached to the gantry
Total wooden boards
 |  |  |  |  |  |  | 35,00 € |  | The price is approxiamete
 |  | PLA |  |  |  |  |  |  | Depending on your 3D printer, you will need a different diameter of PLA
Total |  |  |  |  |  |  | 493,65 € |  | Without taxes or shipping costs (if you look for, there may be cheaper alternatives in your country)

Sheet: optional optical
Components | Unit price | Quantity | Total price | Link | Comments | Alternative:
HEDS-9731 | 16,96 € | 1 | 16,96 € | https://eu.mouser.com/ProductDetail/Broadcom-Avago/HEDS-9731150?qs=sGAEpiMZZMv5XWiOWIxhpAqLKZxboGTyYBFE1yUlXmU%3D | DISCLAIMER: we have not bought or used this one, we used one from a old printer
150 LPI codestrip | 9,10 € | 1 | 9,10 € | https://www.digiprint-supplies.com/en/generic-150-linear-encoder-scale-3-2m-peldi17821 | DISCLAIMER: we have not bought or used this one, we used one from a old printer
2.54mm male Pins | 0,13 € | 1 | 0,13 € | https://eu.mouser.com/ProductDetail/Wurth-Elektronik/61300311121?qs=PhR8RmCirEYxRWFJzNKsUw%3D%3D&vip=1 | Just need a few pins, cut from the strip | https://www.electrocomponentes.es/tira-pines/729-775-tira-40-pines-254mm-simple-macho-negro-single-row-soldar.html
Solder breadboard | 0,59 € | 1 | 0,59 € | https://www.electrocomponentes.es/placas-perforadas/1503-1646-placa-pcb-2x8cm-perforada-doble-cara-254mm-prototipo.html
330 Ohm resistor | 0,09 € | 1 | 0,09 € | https://www.electrocomponentes.es/fijas/34-34-resistencia-330-ohm-025w.html#/38-lotes-lote_1_unidad

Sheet: optional magnetic
 | Components | Unit price | Quantity | Total price | Link | Comments
 | AS5311-TS_EK_AB | 16,17 € | 1 | 16,17 € | https://www.digikey.es/en/products/detail/ams-osram/AS5311-TS-EK-AB/3828353 |  | https://es.rs-online.com/web/p/kits-de-desarrollo-de-sensores/2329691
Alternatives For FPGA Only one Is needed | FPGA | 238,56 € | 1 | 238,56 € | https://shop.trenz-electronic.de/en/29401-Nexys-A7-100T-academic-FPGA-Trainer-Board-Recommended-for-ECE-Curriculum?c=176 | We have used this one because is the one we had available, but you can get a different one, you only need to change the pins of your FPGA, in the design
 | FPGA | 105,32 € | 0 | 0,00 € | https://shop.trenz-electronic.de/en/29002-Arty-S7-Spartan-7-FPGA-for-Makers-and-Hobbyists-with-Xilinx-XC7S25?c=120 | We haven’t try these in this design, but they should work, even cheaper ones
 | FPGA | 49,90 € | 0 | 0,00 € | https://alhambrabits.com/buy/ | We haven’t try these in this design, but they should work, even cheaper ones

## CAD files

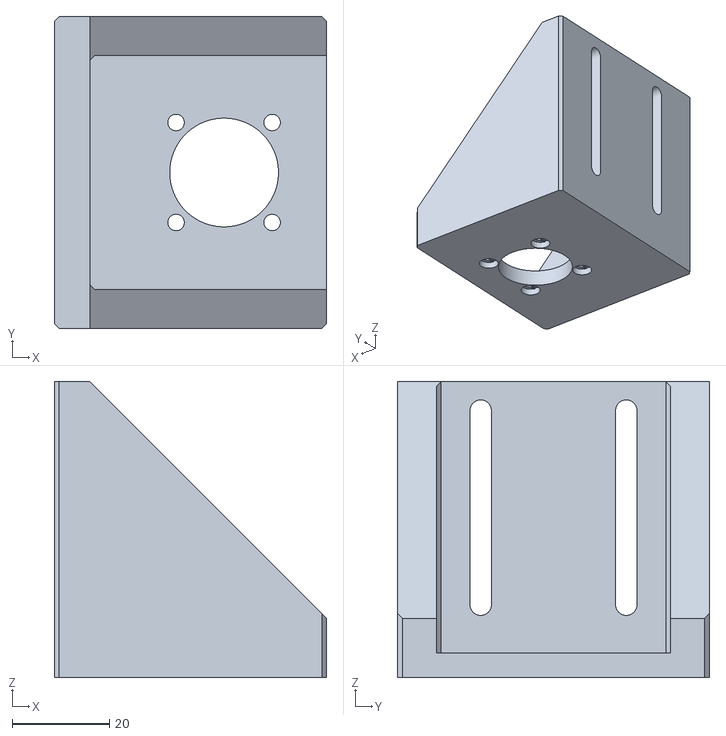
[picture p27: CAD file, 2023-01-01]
assembly/cad/stl/NemaMotorHolder.stl
56.1 x 64.3 x 61.0

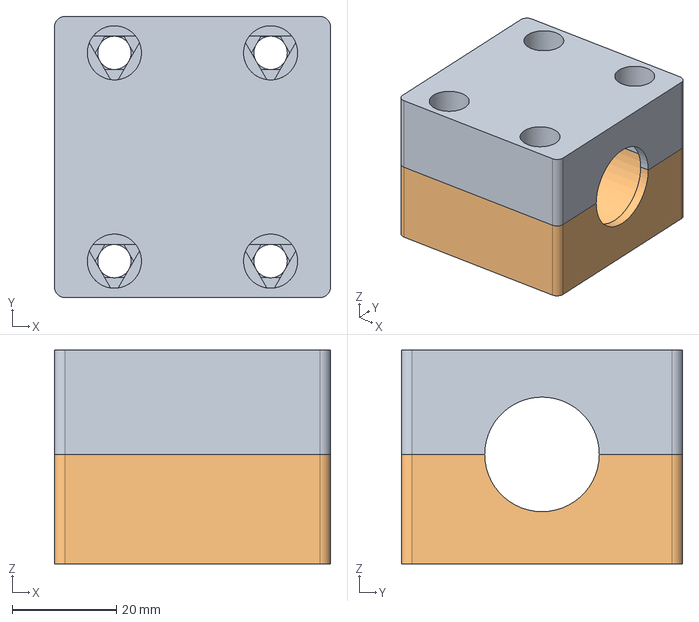
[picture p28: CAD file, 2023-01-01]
assembly/cad/step/linbearhouse.step
53.0 x 54.0 x 41.0 mm
linbearhouse_top
linbearhouse_bot

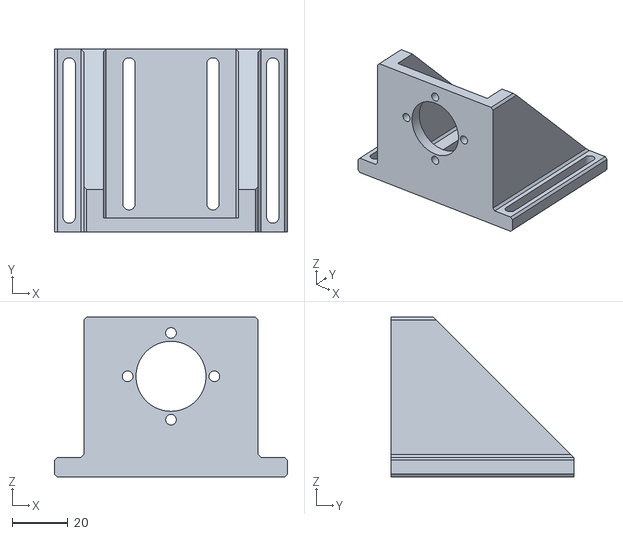
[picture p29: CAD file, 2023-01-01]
assembly/cad/stl/motor_holder_flap.stl
83.3 x 65.2 x 57.1

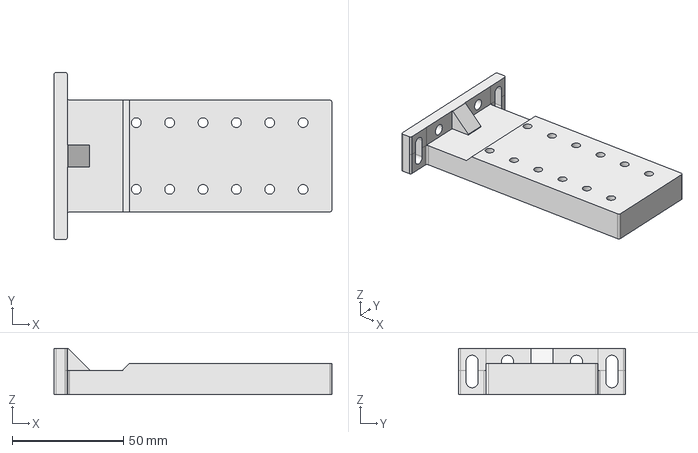
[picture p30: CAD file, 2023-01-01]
assembly/cad/step/motor_base_holder.step
125.0 x 75.3 x 20.8 mm

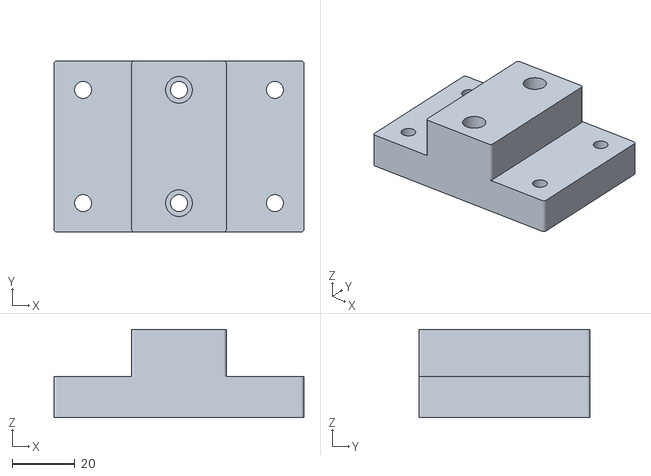
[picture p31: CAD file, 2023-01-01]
assembly/cad/stl/board_class.stl
79.5 x 54.5 x 28.0

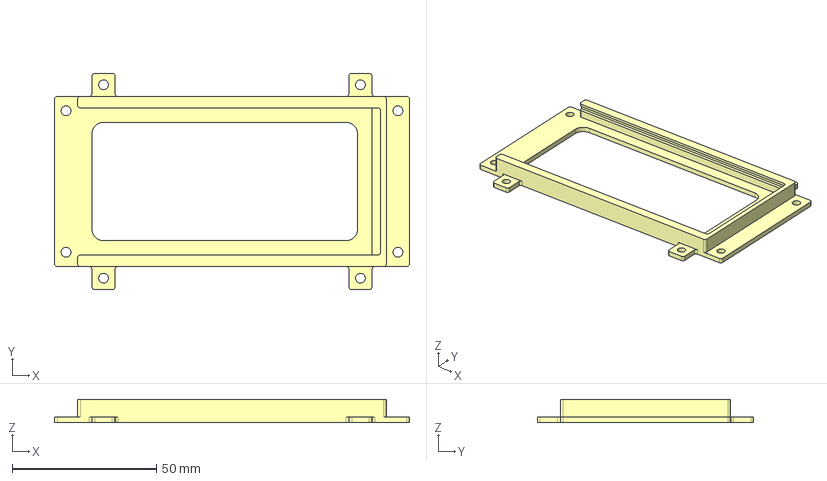
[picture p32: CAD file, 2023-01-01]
assembly/cad/step/arduino_baseplate.step
123.0 x 75.0 x 8.00 mm

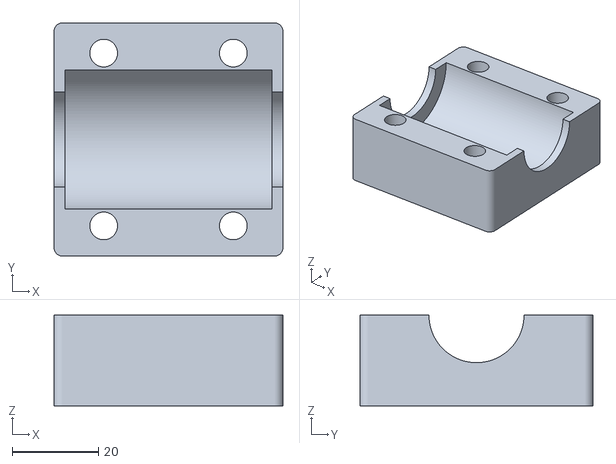
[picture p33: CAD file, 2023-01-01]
assembly/cad/stl/linbearhouse_bot.stl
53.0 x 54.0 x 21.0

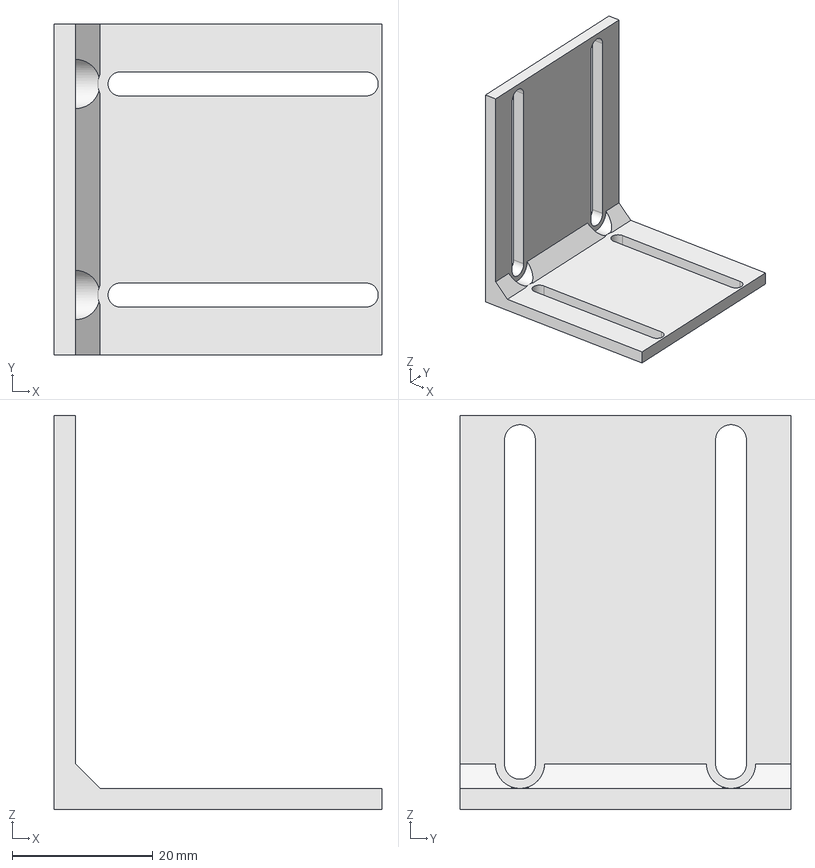
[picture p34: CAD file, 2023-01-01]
assembly/cad/step/optical_sensor_holder.step
46.5 x 47.0 x 56.0 mm

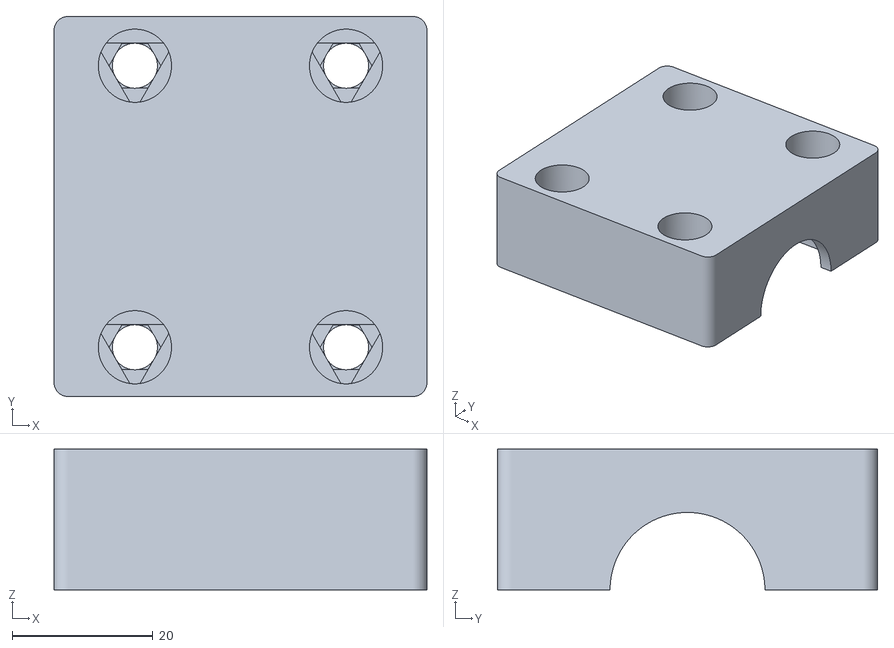
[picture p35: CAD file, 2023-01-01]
assembly/cad/stl/linbearhouse_top.stl
53.0 x 54.0 x 20.0

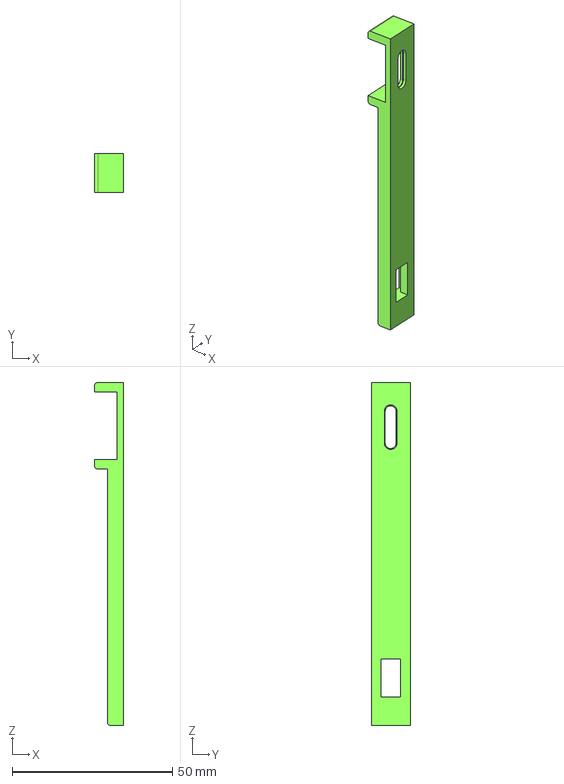
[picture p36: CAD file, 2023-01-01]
assembly/cad/step/endstop_holder.step
9.00 x 12.2 x 107.0 mm

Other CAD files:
assembly/cad/step/motor_holder.step
assembly/cad/step/nut_gantry_joint.step
assembly/cad/freecad/arduino_baseplate.FCStd
assembly/cad/freecad/endstop_holder.FCStd
assembly/cad/freecad/linbearhouse.FCStd
assembly/cad/freecad/motor_base_holder.FCStd
assembly/cad/freecad/motor_holder.FCStd
assembly/cad/freecad/nut_gantry_joint.FCStd
assembly/cad/freecad/optical_sensor_holder.FCStd
assembly/cad/stl/arduino_baseplate.stl
assembly/cad/stl/endstop_holder.stl
assembly/cad/stl/motor_base_holder.stl
assembly/cad/stl/nut_gantry_joint.stl
assembly/cad/stl/optical_sensor_holder.stl

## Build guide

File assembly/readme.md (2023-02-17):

# Assembly

Besides each assembly section, the CAD of the Sandbox can be used as a guide for assembling the Sandbox.

- FreeCAD file: [./cad/freecad/tectoh.FCStd](./cad/freecad/tectoh.FCStd)

FreeCAD is Open Source Software that can be downloaded at no cost: [https://www.freecadweb.org/](https://www.freecadweb.org/)

## CAD

There are some parts that need to be 3D printed, so you will need a 3D printer and some PLA filament.

Parts to 3D print and CAD of the system:

[CAD](./cad/.)

## Mechanical assembly instructions

[Mechanical assembly](./mechanical/.)

## Electronic schematic

[Electronics assembly](./electronics/.)

## Optional parts

The [optional parts](../optional/.) are not required, but the are useful to check that the device is moving as expected.

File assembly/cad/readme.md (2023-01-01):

# CAD

All 3D printed parts are printed with PLA using a layer height of 0.15 or 0.2. It will be necessary to print all with adhesion and without support.

## Motor base holder

Layer height 0.15 mm. Infill 60%

- FreeCAD source file: [./freecad/motor_base_holder.FCStd](./freecad/motor_base_holder.FCStd)
- STEP file: [./step/motor_base_holder.step](./step/motor_base_holder.step)
- STL file to print: [./stl/motor_base_holder.stl](./stl/motor_base_holder.stl)
- Python file to generate FreeCAD file (you need [Maker Workbench](https://github.com/URJCMakerGroup/MakerWorkbench)) : [./py/motor_base_holder.py](./py/motor_base_holder.py)

## Geared NEMA-17 motor holder

Layer height 0.2 mm. Infill 60%

- FreeCAD source file: [./freecad/motor_holder.FCStd](./freecad/motor_holder.FCStd)
- STEP file: [./step/motor_holder.step](./step/motor_holder.step)
- STL file to print: [./stl/motor_holder.stl](./stl/motor_holder.stl)
- Python file to generate FreeCAD file (you need [Maker Workbench](https://github.com/URJCMakerGroup/MakerWorkbench)) : [./py/NemaMotorHolder_class.py](./py/NemaMotorHolder_class.py)

## Joint for Leadscrew Nut - Gantry

This part joints the leadscrew nut with the base of the gantry

Layer height 0.2 mm. Infill 60%

- FreeCAD source file: [./freecad/nut_gantry_joint.FCStd](./freecad/nut_gantry_joint.FCStd)
- STEP file: [./step/nut_gantry_joint.step](./step/nut_gantry_joint.step)
- STL file to print: [./stl/nut_gantry_joint.stl](./stl/nut_gantry_joint.stl)
- Python file to generate FreeCAD file (you need [Maker Workbench](https://github.com/URJCMakerGroup/MakerWorkbench)) : [./py/nut_gantry_joint.py](./py/nut_gantry_joint.py)

## Linear bearing housing

Four pieces are needed for the top and bottom, the top part is 1 mm (21 mm) taller than the bottom part

Layer height 0.15 mm. Infill 60%

- FreeCAD source file: [./freecad/linbearhouse.FCStd](./freecad/linbearhouse.FCStd)
- STEP file: [./step/linbearhouse.step](./step/linbearhouse.step)
- STL file to print the top part: [./stl/linbearhouse_top.stl](./stl/linbearhouse_top.stl)
- STL file to print the bottom part: [./stl/linbearhouse_bot.stl](./stl/linbearhouse_bot.stl) 
- The [Maker Workbench](https://github.com/URJCMakerGroup/MakerWorkbench) can generate configurable linear bearing housings

## Endstop holder

Two pieces are needed (the design needs improvement)

Layer height 0.2 mm. Infill 60%

- FreeCAD source file: [./freecad/endstop_holder.FCStd](./freecad/endstop_holder.FCStd)
- STEP file: [./step/endstop_holder.step](./step/endstop_holder.step)
- STL file to print: [./stl/endstop_holder.stl](./stl/endstop_holder.stl)

## Arduino base support

Layer height 0.2 mm. Infill 40%

- FreeCAD source file: [./freecad/arduino_baseplate.FCStd](./freecad/arduino_baseplate.FCStd)
- STEP file: [./step/arduino_baseplate.step](./step/arduino_baseplate.step)
- STL file to print: [./stl/arduino_baseplate.stl](./stl/arduino_baseplate.stl)
- Python file to generate FreeCAD file (you need [Maker Workbench](https://github.com/URJCMakerGroup/MakerWorkbench)) : [./py/arduino_baseplate.py](./py/arduino_baseplate.py)

## LCD support

These are taken from [Prusa Hefestos](https://github.com/bq/prusa-i3-hephestos)

There is a holder and a hinge:

- FreeCAD source files:
    - [./freecad/lcd-holder.FCStd](./freecad/lcd-holder.FCStd)
    - [./freecad/lcd-hinge.FCStd](./freecad/lcd-hinge.FCStd)
- STEP source files:
    - [./step/lcd-holder.step](./step/lcd-holder.step)
    - [./step/lcd-hinge.step](./step/lcd-hinge.step)
- STL source files:
    - [./stl/lcd-holder.stl](./stl/lcd-holder.stl)
    - [./stl/lcd-hinge.stl](./stl/lcd-hinge.stl)

## Optical sensor holder (Optional)

This is only if you include the optical sensor

Layer height 0.2 mm. Infill 40%

- FreeCAD source file: [./freecad/optendstopical_sensor_holder.FCStd](./freecad/optendstopical_sensor_holder.FCStd)
- STEP file: [./step/optendstopical_sensor_holder.step](./step/optendstopical_sensor_holder.step)
- STL file to print: [./stl/optendstopical_sensor_holder.stl](./stl/optendstopical_sensor_holder.stl)

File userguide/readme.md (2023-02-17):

# User guide

## Welcome screen

At start you will see this screen.

Notice at the bottom-right of the screen that the endstops status are displayed. Check their status before starting the experiment.

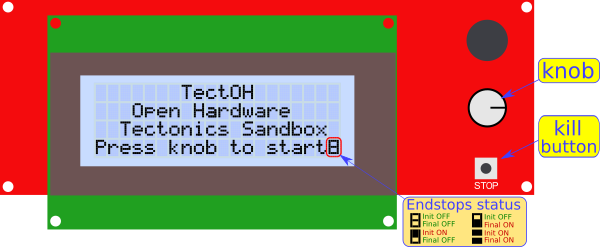
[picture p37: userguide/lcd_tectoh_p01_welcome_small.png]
Welcome screen


[Larger welcome screen](./lcd_tectoh_p01_welcome.png)

## Tasks selection

After you have pressed the knob, you will find a menu in which you can select from these options:

1. Homing (moving to the absolute zero position).
2. Moving a relative distance from where the gantry is
3. Getting information from the last experiment

To select the desired option, turn the knob and push when the desired option is active.

## Homing

If you select this option, you have to choose the speed. From 1 mm/h to 100 mm/h.
Move to the units and tens to select the value.

Once you have selected the speed and distance, select **Go!** to start the experiment. There will be another confirmation message before starting.

## Moving a relative distance

In this option you have to choose the speed (as in the Homing option) and also you have to select the relative distance you want to travel

Once you have selected the speed and distance, select **Go!** to start the experiment. There will be another confirmation message before starting.

## Last experiment info

Displays the information related to the last experiment. Press the knob when you are done.

## Moving

When the Sandbox is moving, it will display the information of the experiment.

Press the **Kill** button to abort the operation

Unless you disconnect the power supply of the Sandbox while moving, it will save the actual position even if it is switched off. This is useful if the preparation of the experiment takes time. So you can move the gantry to the desired position. Prepare the experiment, and then switch on the Sandbox and start the experiment.

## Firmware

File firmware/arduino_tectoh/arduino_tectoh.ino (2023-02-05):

#include "tectoh_config.h"

// Libraries: https://docs.arduino.cc/software/ide-v1/tutorials/installing-libraries
// https://www.arduino.cc/reference/en/libraries/timerone
#include <TimerOne.h>
// https://www.arduino.cc/reference/en/libraries/timerthree
#include <TimerThree.h>
// https://www.arduino.cc/reference/en/libraries/timerfour
#include <TimerFour.h> 

// https://docs.arduino.cc/learn/built-in-libraries/eeprom
// The EEPROM memory keeps its value after powering off, it is very convenient
// to hold the position because:
//  - homing takes a lot of time due to the slow speeds
//  - Setting up the experiment may require hours, so the gantry can be set
//    to its position, then power off the Sandbox to setup the experiment, 
//    and when it is ready, power it up, and start.
//    Te gantry should not go home, because it would ruin the experimet
#include <EEPROM.h>

// LCD library: https://www.arduino.cc/reference/en/libraries/liquidcrystal/
#include <LiquidCrystal.h>

// -------------- LCD and rotary encoder smart controller
// LCD pins
#define LCD_PINS_RS 16      // LCD control RS pin
#define LCD_PINS_ENABLE 17  // LCD enable pin
#define LCD_PINS_D4 23      // LCD data bit 4
#define LCD_PINS_D5 25      // LCD data bit 5
#define LCD_PINS_D6 27      // LCD data bit 6
#define LCD_PINS_D7 29      // LCD data bit 7

// creates a variable of type LiquidCrystal:
// LiquidCrystal(rs, enable, d4, d5, d6, d7)
LiquidCrystal lcd(LCD_PINS_RS, LCD_PINS_ENABLE,
                  LCD_PINS_D4, LCD_PINS_D5,
                  LCD_PINS_D6, LCD_PINS_D7);

// LCD size

#define LCD_NUMCOLS 20  // 20 columns
#define LCD_NUMROWS 4   // 4 rows

#define LCD_PARAMS_COL 12 // column where the parameters are drawn, the left side 

// column where the additional info of the actual position of the gantry according
// to the EEPROM
#define LCD_EEP_POS_COL 11

// Rotary encoder of LCD
#define ROT_ENC1_PIN 31    // Quadrature rotary encoder signal 1
#define ROT_ENC2_PIN 33    // Quadrature rotary encoder signal 1
#define ROT_ENCPB_PIN 35   // Rotary encoder push button

// Beeper
//#define LCD_BEEPER_PIN 33

// LCD stop / kill button
#define LCD_STOP_PIN 41

// ----------- Endstops 
#define ESTOP_INI_PIN 3         // INIT endstop x=0 (HIGH when pressed)
#define ESTOP_END_PIN 2         // END endstop (HIGH when pressed)


// ------------ Stepper motor
#define X_STEP_PIN 54       // STEP pin for the first stepper motor driver (axis X)
#define X_DIR_PIN 55        // DIR pin for the first stepper motor driver (axis X)
#define X_ENABLE_PIN 38     // ENABLE pin for the first stepper motor driver (axis X)

// defined in configuration file: tectoh_config.h
#if DIR_MOTOR_POSITIVE_HIGH
  #define DIR_MOTOR_POS HIGH
  #define DIR_MOTOR_NEG LOW
#else
  #define DIR_MOTOR_POS LOW
  #define DIR_MOTOR_NEG HIGH
#endif

#if ENABLE_MOTOR_LOW
  #define ENABLE_MOTOR  LOW
  #define DISABLE_MOTOR HIGH
#else
  #define ENABLE_MOTOR  HIGH
  #define DISABLE_MOTOR LOW
#endif

#if LCD_STOP_BTN_ACTIVE_HIGH
  #define STOP_BTN_ON   HIGH
  #define STOP_BTN_OFF  LOW
#else
  #define STOP_BTN_ON   LOW
  #define STOP_BTN_OFF  HIGH
#endif

// ------------ Linear position sensor LPS
  
#define LPS_ENC1_PIN  20  // Linear position encoder 1 pin
#define LPS_ENC2_PIN  21  // PIN del canal B del encoder


// in 400 mm there are about 2362 lines, so a int, or a short is enough
volatile short lps_line_cnt = 0;    // number of counted lines of the linear position sensor
const float mm_per_lps_line = 0.1693; // milimiters per line from linear pos sensor

// --- endstop values
byte estop_ini;    // endstop value at x=0
byte estop_end;    // endstop value at the end

// defined in configuration file: tectoh_config.h
#if ESTOP_ACTIVE_HIGH
  #define ESTOP_ON  HIGH
  #define ESTOP_OFF LOW
#else
  #define ESTOP_ON  LOW
  #define ESTOP_OFF HIGH
#endif

const int TOT_LEN = 270;    // leadscrew length in mm, maximum distance
const int MAX_VEL = 100;    // maximum velocity in mm/h

const int LEAD = 3;  // lead screw lead in mm. How many mm advances per revolution
const int STEP_REV = 200; // how many steps per revolution the motor has
const int HSTEP_REV = 2 * STEP_REV; // halfsteps per revolution

const float GEAR_R = 51.0f; // gear ratio of the motor

//advance in mm per halfstep  3 / (270 * 51) = 0.000 147
//const float ADVAN_HSTEP = float(LEAD) / (HSTEP_REV * GEAR_R);
const float ADVAN_HSTEP = 0.000147;

// ---- variables for keeping track the experiment timing

// and experiment could take 400 hours if 400 mm at 1mm/h, it is not likely
// but just in case, make it short, not byte
volatile short hour_cnt = 0;        // Keep track of the number of hours of the experiment
volatile byte minute_cnt = 0;       // Keep track of the number of minutes of the experiment
volatile byte sec_cnt = 0; // Keep track of the number of seconds of the experiment

// ----- Sandbox parameters

// EEPROM DATA

//#define EEPROM_DIR 0  // memory address of the EEPROM where the gantry position is

// ----------------- EEPROM addresses 

// 1 Valid, 0 not valid (defined by EEP_VALID_DATA, EEP_INVALID_DATA)
#define EEP_AD_VALID 0

// Actual position in mm: 0 to 400, short. 2 bytes
#define EEP_AD_POS_ACT 24

// Last experiment values
// Distance last experiment. 2 bytes
// with sign
#define EEP_AD_DIST  3

// original position of the previous experiment
#define EEP_AD_POS_PREV 5 // 2 bytes
// So we have: [EEP_AD_POS_ACT] = [EEP_AD_POS_PREV] + [EEP_AD_DIST]

// Speed last experiment. short. 2 bytes
// could be just 1 byte, but in case we get larger speeds
#define EEP_AD_VEL   7

// Time last experiment. 1 byte
#define EEP_AD_SECS  9
#define EEP_AD_MINS  10 // 1 byte
#define EEP_AD_HOURS 11 // 2 bytes

// distance calculated from halfsteps
#define EEP_AD_DIST_HS  13  // 2 bytes

// distance calculated from counting lines
#define EEP_AD_DIST_LINE  15  // 2 bytes

// number of halfsteps unsigned long 32 bits: 4 bytes
#define EEP_AD_HS_CNT  17  // 4 bytes

// number of lines short 16 bits: 2 bytes. less than 3000 lines
// can be positive or negative
#define EEP_AD_LINE_CNT  21  // 2 bytes

// state of the endstops
#define EEP_AD_ESTOP   23  // 1 bytes

#define EEP_BIT_ESTOP_INI 0 // in the bit 0 of address EEP_AD_ESTOP
#define EEP_BIT_ESTOP_END 1 // in the bit 1 of address EEP_AD_ESTOP

// bits to make the mask
#define EEP_MASK_ESTOP_INI 1<<EEP_BIT_ESTOP_INI // bit 0 of ad EEP_AD_ESTOP
#define EEP_MASK_ESTOP_END 1<<EEP_BIT_ESTOP_END // bit 1 of ad EEP_AD_ESTOP

// EEPPROM address EEP_AD_VALID
#define EEP_VALID_DATA   1 //data from EEPROM is valid
#define EEP_INVALID_DATA 0 //data from EEPROM is not valid
#define EEP_ESTOP_ERR    2 //postion and endstop info doesnt match

byte  eeprom_valid_read = EEP_INVALID_DATA;  // 0
short pos_act_eep_read  =  0;  // 1,2
short dist_eep_read     =  0;  // 3,4
short pos_prev_eep_read =  0;  // 5,6
short vel_eep_read      =  0;  // 7,8
byte  secs_eep_read     =  0;  // 9
byte  mins_eep_read     =  0;  // 10
short hours_eep_read     =  0; // 11,12
short dist_hs_eep_read   =  0; // 13,14 positive
short dist_line_eep_read =  0; // 15,16 pos o neg
// Number of half steps counted. a long has 32 bits -> being unsigned
// from 0 to 4,294,967,295
// 400 mm, with 3mm lead, 400 halfsteps per turn and 51 reduction,
// gives 0,147 um/halfstep, which is 
//               2,714,666.67 halfsteps (22 bits) So we can count them
unsigned long  hs_cnt_eep_read    =  0; // 17,18,19,20
short line_cnt_eep_read  =  0; // 21,22 pos o neg
byte estop_ini_eep_read = 0; //23 taken from the same address
byte estop_end_eep_read = 0; //23


// short are 16bits
// Speed of the Sandbox in mm/h, from 1 to 100, making it short, to have negative
// to make some operations
short vel_mmh = MAX_VEL;  // Speed of the Sandbox in mm/h, from 1 to 100
short pos_dest = 0;  // absolute position of the destination, from x0 in mm
//experiment's distance to the destination in mm, Magnitude (no sign)
short dist_dest_magn = 1; //experiment's distance to the destination in mm, no sign 
short dist_dest_wsign = 1; // relative position of the destination, with sign
bool  is_dist_dest_neg = false;  //sign of dist_dest_magn: false: positive, true: negative

volatile byte h_ustp_cnt = 0;    // Number of half usteps in a halfstep 0 to 31

// Number of half steps counted. a long has 32 bits -> being unsigned
// from 0 to 4,294,967,295
// 400 mm, with 3mm lead, 400 halfsteps per turn and 51 reduction,
// gives 0,147 um/halfstep, which is 
//               2,714,666.67 halfsteps (22 bits) So we can count them
volatile unsigned long hstp_cnt = 0;   // Number of half steps, from initial position

// traveled distance in the experiment
// Calculated from steps
float traveled_mm_hs_f = 0; // float version calculated from halfsteps
short traveled_mm_hs = 0; //  converted integer version

// Calculated from lines
float traveled_mm_lin_f = 0; // float version, will be converted calculated from lines
short traveled_mm_lin = 0; // calculated from lines
 

// array for the time of a half of a microstep (half time low, half high)
// For  3mm lead, 400 halfsteps per turn and 51 reduction, the fastest
// speeds, from 83mm/h and up, the h_ustp take less than 200 us
// for speed from 1mm/h to 82 mm/h, the h_microstp take 200 us
// This vector should be integer, because we are not usign decimals AAAAA

const float vec_t_h_ustp[] = {0,200,200,200,200,200,200,200,200,200,200,200,200,200,200,200,200,200,200,200,200,200,200,200,200,200,200,200,200,200,200,200,200,200,200,200,200,200,200,200,200,200,200,200,200,200,200,200,200,200,200,200,200,200,200,200,200,200,200,200,200,200,200,200,200,200,200,200,200,200,200,200,200,200,200,200,200,200,200,200,200,200,200,199.33,196.95,194.64,192.37,190.16,188.00,185.89,183.82,181.80,179.83,177.89,176.00,174.15,172.33,170.56,168.82,167.11,165.44};

// it is byte because is less than 200
byte t_half_ustp; // time that a half microstep takes, from the previous vector
const byte SLEW_VEL_T_H_USTP = 200; // microseconds lower than the speed will be continuos

// array for the time of a half step (h_stp), it is only used when the time
// a half microstep (h_ustp) is 200. i.e. for slow speeds.
// Otherwise, they would be out of sync
const float vec_t_h_stp[] = {0,529411.76,264705.88,176470.59,132352.94,105882.35,88235.29,75630.25,66176.47,58823.53,52941.18,48128.34,44117.65,40723.98,37815.13,35294.12,33088.24,31141.87,29411.76,27863.78,26470.59,25210.08,24064.17,23017.90,22058.82,21176.47,20361.99,19607.84,18907.56,18255.58,17647.06,17077.80,16544.12,16042.78,15570.93,15126.05,14705.88,14308.43,13931.89,13574.66,13235.29,12912.48,12605.04,12311.90,12032.09,11764.71,11508.95,11264.08,11029.41,10804.32,10588.24,10380.62,10181.00,9988.90,9803.92,9625.67,9453.78,9287.93,9127.79,8973.08,8823.53,8678.88,8538.90,8403.36,8272.06,8144.80,8021.39,7901.67,7785.47,7672.63,7563.03,7456.50,7352.94,7252.22,7154.21,7058.82,6965.94,6875.48,6787.33,6701.41,6617.65,6535.95,6456.24,6378.45,6302.52,6228.37,6155.95,6085.19,6016.04,5948.45,5882.35,5817.71,5754.48,5692.60,5632.04,5572.76,5514.71,5457.85,5402.16,5347.59,5294.12};


// ---------------- FINITE STATE MACHINES (FSM)
// There are 3:
//  - ui_state: the main FSM of the user interface (UI),
//               indicate the main activity
//  - selparam_st: indicates which parameter is being changed
//  - seldigit_st: indicates which digit is being changed

#define   ST_INI        0   // initial state, welcome
#define   ST_SEL_TASK   1   // Task selection: GO HOME - Move
#define   ST_SEL_PARAMS 2   // Selecting the parameters: speed, distance
#define   ST_SEL_DIGIT  3   // Setting the digit
#define   ST_SEL_VALUE  4   // Setting the digit value
#define   ST_CONFIRM    5   // Confirming to start
#define   ST_HOMING     6   // Homing
#define   ST_RUN        7   // Running the experiment
#define   ST_LAST_INFO  8   // Info last experiment  
#define   ST_END        9   // Moving ended

byte ui_state = ST_INI;
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

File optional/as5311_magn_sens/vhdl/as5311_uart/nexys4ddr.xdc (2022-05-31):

## This file is a general .xdc for the Nexys4 DDR Rev. C
## To use it in a project:
## - uncomment the lines corresponding to used pins
## - rename the used ports (in each line, after get_ports) according to the top level signal names in the project

## Clock signal
set_property -dict { PACKAGE_PIN E3    IOSTANDARD LVCMOS33 } [get_ports { clk }]; #IO_L12P_T1_MRCC_35 Sch=clk100mhz
create_clock -add -name sys_clk_pin -period 10.00 -waveform {0 5} [get_ports {clk}];


##Switches

set_property -dict { PACKAGE_PIN J15   IOSTANDARD LVCMOS33 } [get_ports { sw[0] }]; #IO_L24N_T3_RS0_15 Sch=sw[0]
set_property -dict { PACKAGE_PIN L16   IOSTANDARD LVCMOS33 } [get_ports { sw[1] }]; #IO_L3N_T0_DQS_EMCCLK_14 Sch=sw[1]
set_property -dict { PACKAGE_PIN M13   IOSTANDARD LVCMOS33 } [get_ports { sw[2] }]; #IO_L6N_T0_D08_VREF_14 Sch=sw[2]
set_property -dict { PACKAGE_PIN R15   IOSTANDARD LVCMOS33 } [get_ports { sw[3] }]; #IO_L13N_T2_MRCC_14 Sch=sw[3]
set_property -dict { PACKAGE_PIN R17   IOSTANDARD LVCMOS33 } [get_ports { sw[4] }]; #IO_L12N_T1_MRCC_14 Sch=sw[4]
set_property -dict { PACKAGE_PIN T18   IOSTANDARD LVCMOS33 } [get_ports { sw[5] }]; #IO_L7N_T1_D10_14 Sch=sw[5]
set_property -dict { PACKAGE_PIN U18   IOSTANDARD LVCMOS33 } [get_ports { sw[6] }]; #IO_L17N_T2_A13_D29_14 Sch=sw[6]
set_property -dict { PACKAGE_PIN R13   IOSTANDARD LVCMOS33 } [get_ports { sw[7] }]; #IO_L5N_T0_D07_14 Sch=sw[7]
set_property -dict { PACKAGE_PIN T8    IOSTANDARD LVCMOS18 } [get_ports { sw[8] }]; #IO_L24N_T3_34 Sch=sw[8]
set_property -dict { PACKAGE_PIN U8    IOSTANDARD LVCMOS18 } [get_ports { sw[9] }]; #IO_25_34 Sch=sw[9]
set_property -dict { PACKAGE_PIN R16   IOSTANDARD LVCMOS33 } [get_ports { sw[10] }]; #IO_L15P_T2_DQS_RDWR_B_14 Sch=sw[10]
set_property -dict { PACKAGE_PIN T13   IOSTANDARD LVCMOS33 } [get_ports { sw[11] }]; #IO_L23P_T3_A03_D19_14 Sch=sw[11]
set_property -dict { PACKAGE_PIN H6    IOSTANDARD LVCMOS33 } [get_ports { sw[12] }]; #IO_L24P_T3_35 Sch=sw[12]
set_property -dict { PACKAGE_PIN U12   IOSTANDARD LVCMOS33 } [get_ports { sw[13] }]; #IO_L20P_T3_A08_D24_14 Sch=sw[13]
set_property -dict { PACKAGE_PIN U11   IOSTANDARD LVCMOS33 } [get_ports { sw[14] }]; #IO_L19N_T3_A09_D25_VREF_14 Sch=sw[14]
set_property -dict { PACKAGE_PIN V10   IOSTANDARD LVCMOS33 } [get_ports { sw[15] }]; #IO_L21P_T3_DQS_14 Sch=sw[15]


## LEDs
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

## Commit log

2022-05-21 Initial version of Arduino firmware
2022-05-21 Continue refactoring Arduino code
2022-05-21 Create lcdprint_rght to print numbers right align
2022-05-23 Arduino code refactoring continuation
2022-05-23 Print endstop state + read from EEPROM
    Not yet writting to the EEPROM
2022-05-24 Fix bug in confirm menu + no travel 0mm
    There was a missing break in the case
    travel distances should not be 0, fixed in the selection menu
2022-05-24 Finish homing screen + add chars + add config.h
    config.h for the motor direction
    add chars to fit everything in homing screen
2022-05-25 Fix bugs: writting EEPROM + disabling motor
2022-05-28 Minor changes, change EEPROM address
    It wasnt working the final experiment address, that would become
    the intitial. Changed to another address, and now works
    I dont know if it is that the particular EEPROM address of my arduino is
    corrupted, or other error, but now it works
2022-05-29 Fix bug converting halfsteps to mm
    It rounded, so at >0.5 mm, it would be 1 mm and finished
    Now it uses floor and works well
2022-05-31 Linear sensor AS5311 with UART data sending
    Explanation in readme file
2022-06-01 Change FPGA constraint files (#23)
    To better identify the FPGA board used
2022-09-25 Add python filter magnetic encoder
2022-09-25 Add double mean filter (python)
2022-09-25 Process sensor data to consider overflow
2022-09-25 Impove median filter and interpolation (python)
2022-09-25 Magnetic sensor data with real distance units
2022-09-26 Filtered magnetic encoder data to csv (python)
2022-09-28 Python script to plot magnetic sensor data
2022-11-09 Process magnetic sensor data when monotonic
    The gantry is always moving forward
2022-11-12 Python to cut raw files in individual experiments
    Some data raw files have varios experiments in it
    so divide the file into more manageable files
2022-11-14 MagnSen: include 2nd pass moving average filter
2022-12-26 MagnSens: Fix cut time for an experiment
    modified: electronics/magn_sensor_analysis/cut_binary_files.py
2022-12-26 MagnSens: temporal latest version proc_mang_sensor
    These files will be substituted by
    magn_sensor_analysis/proc_magn_sensor_lp.py
    but to keep their latest version before deleting them, just in case
    modified: magn_sensor_analysis/proc_magn_sensor.py
    modified: magn_sensor_analysis/procfwd_magn_sensor.py
2022-12-29 Improve documentation + CAD files
    [NemaMotorHolder.stl, arduino_cover.stl, board_class.stl, endstop_holder.FCStd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]
2022-12-29 Add CAD for complete Sandbox + some parts
    [arduino_baseplate.FCStd, arduino_baseplate.step, arduino_baseplate.stl, arduino_cover.stl]
2022-12-30 Document the optical sensor
2022-12-31 user guide + optical sensor doc + CAD model
2022-12-31 Add BOM + improve documentation
    [tectoh_bom.ods]
2023-01-06 Include optional components in BOM + improve doc
    [tectoh_bom.ods]
2023-02-05 Fix misleading comment in Arduino comment
    modified: firmware/arduino_tectoh/arduino_tectoh.ino
